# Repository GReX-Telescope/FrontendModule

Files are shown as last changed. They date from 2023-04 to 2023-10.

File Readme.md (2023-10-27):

# GReX Frontend Module

You'll need:
- [Rust](https://rustup.rs/)
- ARM Rust toolchain
    - `rustup target add thumbv7em-none-eabihf`
- [just](https://github.com/casey/just)
    - `cargo install just`
- [cross](https://github.com/cross-rs/cross) (which requires either Docker or Podman)
    - `cargo install cross --git https://github.com/cross-rs/cross`
- [probe-rs](https://probe.rs/)
    - `cargo install probe-rs --features cli,ftdi`

## Hardware

For assembly, access the interactive BOM [here](https://grex-telescope.github.io/FrontendModule/hardware/bom/ibom.html)

## Software

### Building

Build for the current architecture

`just build-cli`

### For the RPi in the box

`just build-cli-pi`

The resulting binary is in `target/armv7-unknown-linux-musleabihf/release/cli` which you can copy to the Pi, `chmod +x` if you need, and run.

## Firmware

### Building

`just build-firmware`

The resulting binary (elf) is in target/thumbv6m-none-eabi/release/firmware

### Flashing

Using a JLink in CMSIS-DAP mode

`just flash-firmware`

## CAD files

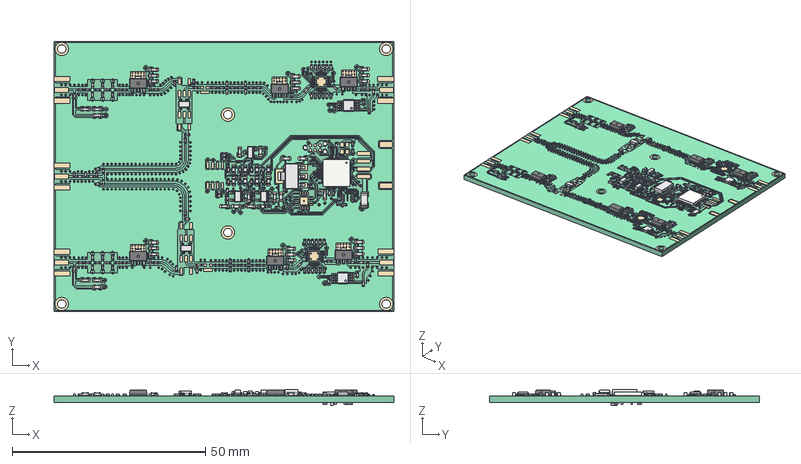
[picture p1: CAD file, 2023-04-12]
hardware/FreeCAD_Render.FCStd
88.0 x 70.0 x 4.27 mm
Pcb_5cf6
topPads_5cf6
topTracks_5cf6
topZones_5cf6
botPads_5cf6
botTracks_5cf6
botZones_5cf6
R35_R_0402_1005Metric_f5f3ad6d96c7 x 39
U27_MSOP_8_3x3mm_P065mm_f5ce7eb6c5d4 x 2
C12_C_0603_1608Metric_8642f7516920 x 30
C99_C_0402_1005Metric_0b61def5e92b x 70
L20_L_0402_1005Metric_fefcc591d3d4 x 34
D1_LED_0603_1608Metric_cfe29d252c61 x 8
R7_R_0603_1608Metric_f544fe8919fd x 3
adbeea57-9c39-11ed-93f0-dde97e994e83_part x 6
adbeea58-9c39-11ed-93f0-dde97e994e83_part x 6
adbeea59-9c39-11ed-93f0-dde97e994e83_part x 6
L6_L_0603_1608Metric_c72d023e8189 x 4
U4_SOT_223_62a9cd10a710
F1_Fuse_1206_3216Metric_ddd44b4a31ef
U7_SOT_23_5_c46f7dd765f9 x 2
U6_QFN_56_1EP_7x7mm_P04mm_EP32x32mm_00caf949446c
U12_SOT_143_13a6a7517807 x 2
U3_SOT_23_b6f0decfda9a

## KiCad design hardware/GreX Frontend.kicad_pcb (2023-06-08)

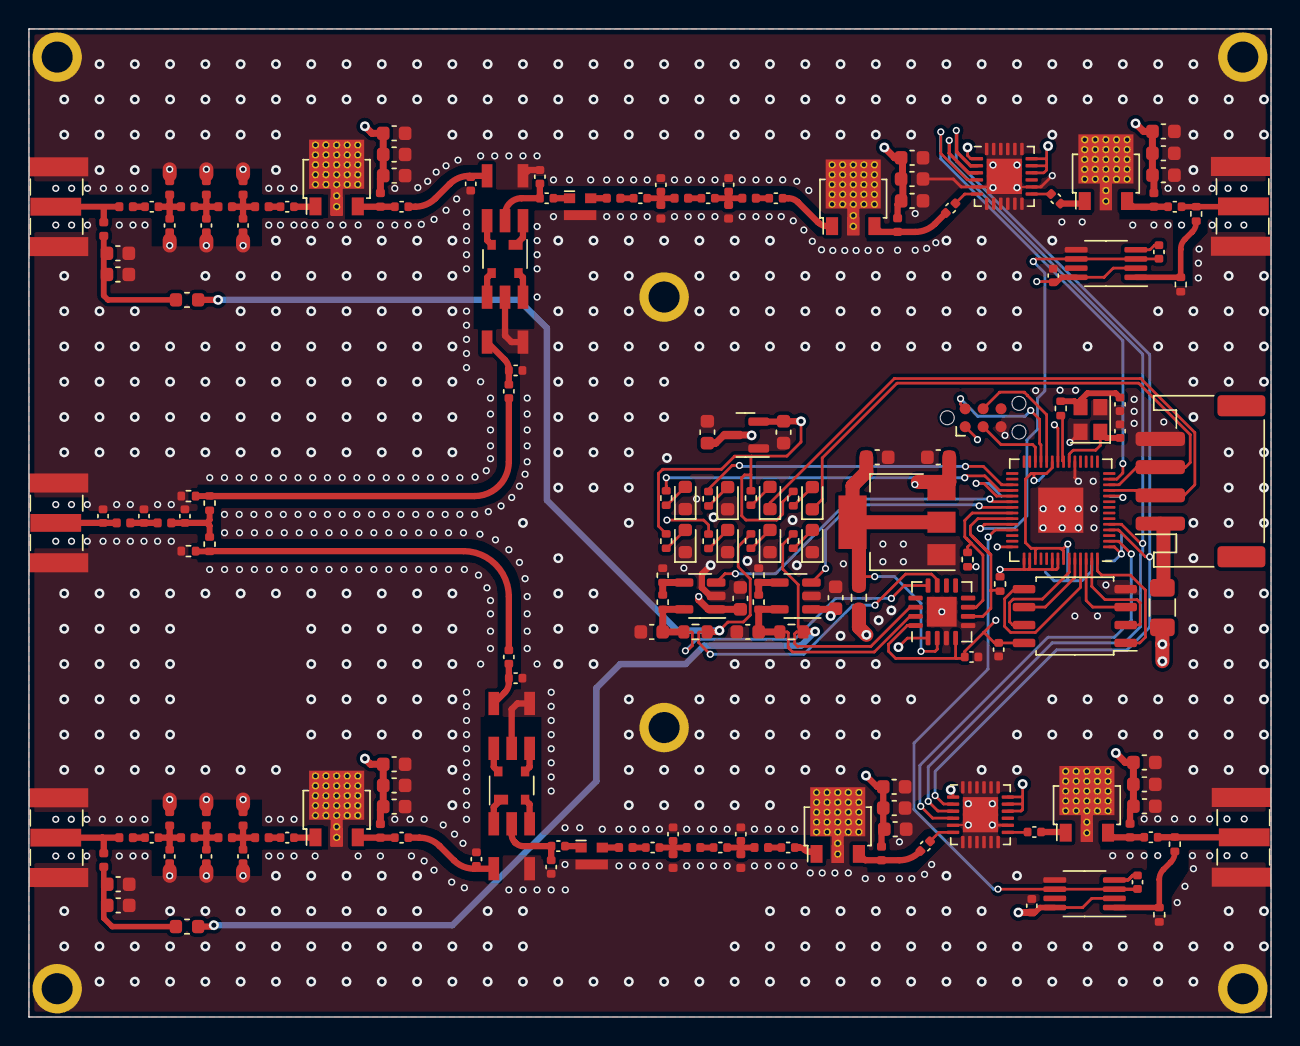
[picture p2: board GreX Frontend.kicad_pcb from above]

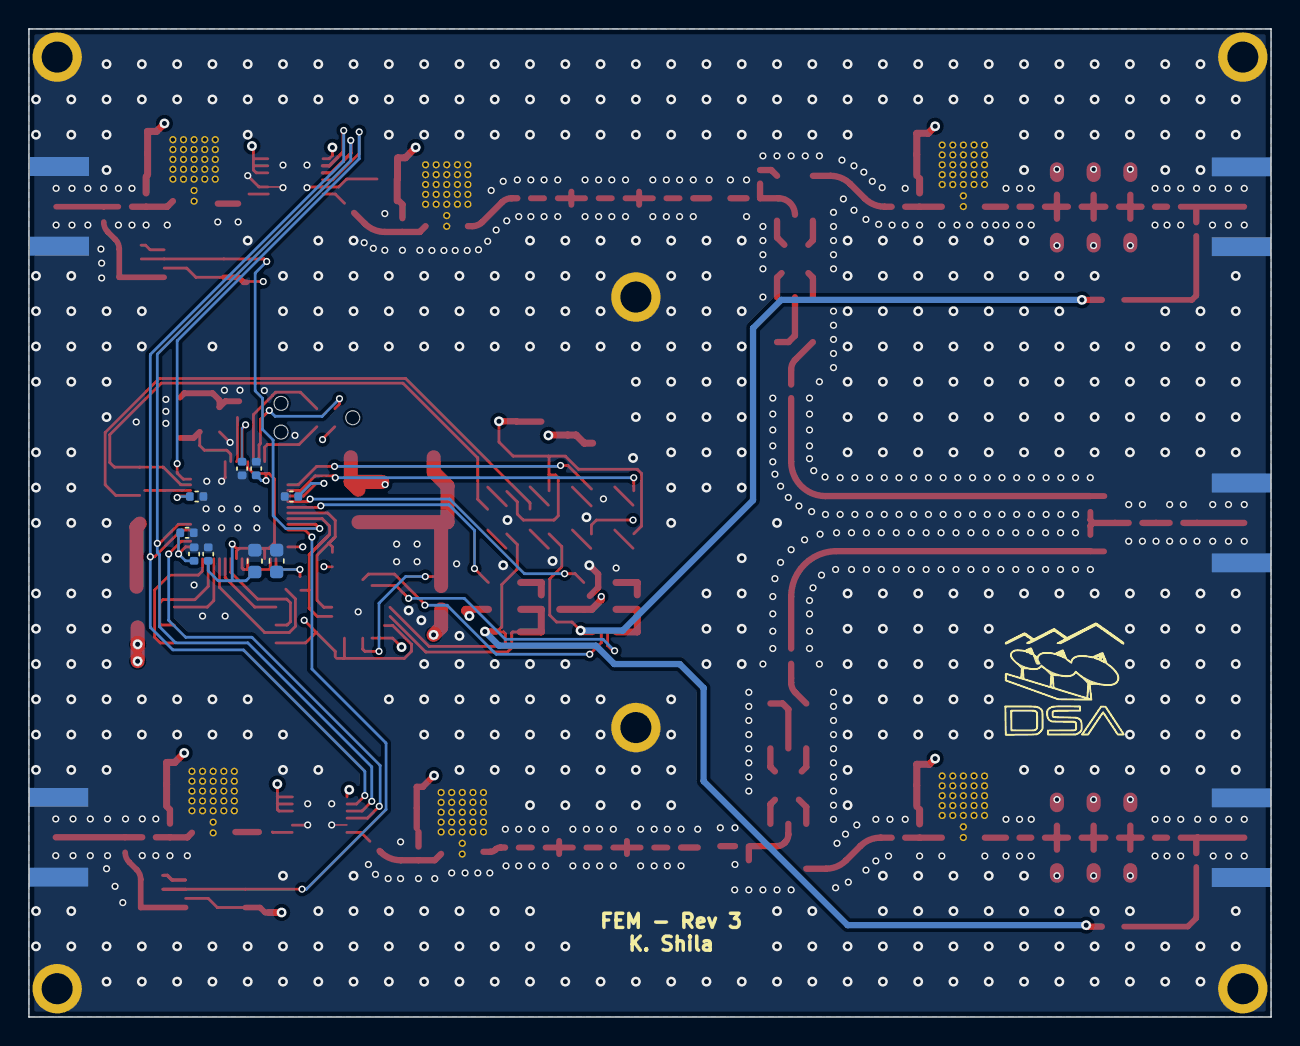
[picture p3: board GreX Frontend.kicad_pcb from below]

Board: 4 copper layers, 88.0 x 70.0 mm, 199 parts (10 on the bottom side), 116 nets.

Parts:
C1, C34, C38, C52, C55, C59, C75, C79: 1.2n; C_0603_1608Metric
C2, C35, C39, C53, C56, C60, C76, C80: 68p; C_0603_1608Metric
C3, C4, C5, C7, C9, C10, C17, C19, C33, C40, C54, C61, C74, C78: 1u; C_0603_1608Metric
C6, C8: 22u; C_0603_1608Metric
C11, C13, C15, C16, C18, C20, C21, C22, C23, C29, C30, C31, C32, C36, C37, C41, C57, C58, C62, C77, C81, C82, C87: 100n; C_0402_1005Metric
C12, C14: 15p; C_0402_1005Metric
C24, C28, C42, C46: 8.2p; C_0402_1005Metric
C25, C27, C43, C45: 16p; C_0402_1005Metric
C26, C44: 3.9p; C_0402_1005Metric
C47, C51, C69, C73: 1.3p; C_0402_1005Metric
C48, C50, C70, C72: 5p; C_0402_1005Metric
C49, C71: 1.6; C_0402_1005Metric
C63, C65: 1.8p; C_0402_1005Metric
C64: 4p; C_0402_1005Metric
C66, C67, C68, C83, C84, C85, C86, C88: DNP; C_0402_1005Metric
D1, D2, D3, D4: RED; LED_0603_1608Metric
D5, D6: GREEN; LED_0603_1608Metric
D7, D8: BLUE; LED_0603_1608Metric
F1: Polyfuse; Fuse_1206_3216Metric
H1, H2, H3, H4, H5, H6: MountingHole_2.2mm_M2_ISO7380_Pad
J1, J4, J5, J6, J7: Conn_Coaxial; SMA_Samtec_SMA-J-P-X-ST-EM1_EdgeMount
J2: Screw_Terminal_01x04; JST_PH_S4B-PH-SM4-TB_1x04-1MP_P2.00mm_Horizontal
J3: PROG; Tag-Connect_TC2030-IDC-NL_2x03_P1.27mm_Vertical
L1, L22: 47u; L_0603_1608Metric
L2, L23, L35, L36: 43n; L_0402_1005Metric
L3, L7, L10, L14: 24n; L_0402_1005Metric
L4, L6, L11, L13: 12n; L_0402_1005Metric
L5, L12: 51n; L_0402_1005Metric
L8, L9, L24, L25: 1000n; L_0402_1005Metric
L15, L21, L28, L34: 8.7n; L_0402_1005Metric
L16, L20, L29, L33: 2.2n; L_0402_1005Metric
L17, L19, L30, L32: 13n; L_0402_1005Metric
L18, L31: 27n; L_0402_1005Metric
L26, L27: 9.1n; L_0402_1005Metric
R1, R3: 82k; R_0402_1005Metric
R2, R4: 24k; R_0402_1005Metric
R5: 0.2; R_0603_1608Metric
R6, R7: 1; R_0603_1608Metric
R8, R9, R10, R11, R12, R13, R14, R15, R16: 1k; R_0402_1005Metric
R17, R18: 4.7k; R_0402_1005Metric
R19, R22: 100; R_0402_1005Metric
R20, R21: 68; R_0402_1005Metric
R23, R25: 226; R_0402_1005Metric
R24, R26: 28; R_0402_1005Metric
U1: DSA_Logo; DSAlogo_letterswhite
U2: XC6206PxxxMR; SOT-23
U3: AMS1117-5.0; SOT-223-3_TabPin2
U4, U5: SPX3819M5-L; SOT-23-5
U6: INA3221; Texas_RGV_S-PVQFN-N16_EP2.1x2.1mm
U7: IS25LP080D-JBLE; SOIC-8_5.275x5.275mm_P1.27mm
U8: RP2040; QFN-56-1EP_7x7mm_P0.4mm_EP3.2x3.2mm
U9, U10: PAT1220-C-3DB; RF_Attenuator_Susumu_PAT1220
U11, U13, U14, U16, U20, U21: ADL5611; SOT89-HighTemp
U12, U15: HMC1122; LFCSP-24-1EP_4x4mm_P0.5mm_EP2.5x2.5mm
U17, U19, U23, U25: TC4-19G2; AT224
U18, U24: BAT-15-099R; SOT-143
U22, U26: AD8314; MSOP-8_3x3mm_P0.65mm
Y1: 2TJ412000NYGBC; Crystal_SMD_2520-4Pin_2.5x2.0mm

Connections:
+1V1: C15.1, C16.1, C17.2, U8.23 (DVDD), U8.45 (VREG_VOUT), U8.50 (DVDD)
+3V3: C7.2, C11.1, C13.1, C18.1, C19.2, C20.1, C21.1, C22.1, C23.1, J3.1, R8.1, R14.1, R15.1, R17.1, R18.1, U2.2 (VO), U6.4 (VS), U6.16 (VPU), U7.8 (VCC), U8.1 (IOVDD), U8.10 (IOVDD), U8.22 (IOVDD), U8.33 (IOVDD), U8.42 (IOVDD), U8.43 (ADC_AVDD), U8.44 (VREG_IN), U8.48 (USB_VDD), U8.49 (IOVDD)
+5VA: C33.2, C34.2, C35.2, C38.2, C39.2, C40.2, C54.2, C55.2, C56.2, C59.2, C60.2, C61.2, C74.2, C75.2, C76.2, C78.2, C79.2, C80.2, C82.2, C87.2, L8.1, L9.1, L24.1, L25.1, L35.1, L36.1, R5.2, R9.1, U6.1 (IN-3), U12.1 (P/S), U12.16 (PUP2), U12.17 (PUP1), U12.18 (VDD), U15.1 (P/S), U15.16 (PUP2), U15.17 (PUP1), U15.18 (VDD), U22.2 (ENBL), U22.8 (VPOS), U26.2 (ENBL), U26.8 (VPOS)
/RF/IF Filter 1 /In: L3.1, U9.2
/RF/IF Filter 1 /Out: C28.2, U11.1
/RF/IF Filter 2/In: L10.1, U10.2
/RF/IF Filter 2/Out: C46.2, U14.1
/RF/Input Stage 1/ADL5611/In: C51.1, U20.1
/RF/Input Stage 1/Input Filter/In: J1.1 (In), L2.2, L15.1
/RF/Input Stage 1/OUT: C77.1, C84.1, U23.4
/RF/Input Stage 2/ADL5611/In: C73.1, U21.1
/RF/Input Stage 2/Input Filter/In: J6.1 (In), L23.2, L28.1
/RF/Input Stage 2/OUT: C66.1, C81.1, U17.6 (PD)
/RF/LO Filter/In: C63.1, J4.1 (In), L26.1
/RF/LO Filter/Out: C65.1, L27.2, R20.1, R21.2
/RF/Mixer/IF: C32.1, C67.1, U17.2 (SCT)
/RF/Mixer/LO: C29.2, C68.1, U19.4
/RF/Mixer_1/IF: C31.1, C85.1, U23.2 (SCT)
/RF/Mixer_1/LO: C30.2, C86.1, U25.6 (PD)
/RF/Output Stage 1/Power Sensor/RF_In: C41.2, J5.1 (In), R23.1
/RF/Output Stage 2/Power Sensor/RF_In: C62.2, J7.1 (In), R25.1
ATTEN_LE_1: U8.13 (GPIO10), U12.4 (LE)
ATTEN_LE_2: U8.2 (GPIO0), U15.4 (LE)
CLK: U8.4 (GPIO2), U12.2 (CLK), U15.2 (CLK)
GND: C1.1, C2.1, C3.1, C4.1, C5.1, C6.1, C7.1, C8.1, C9.1, C10.1, C11.2, C12.2, C13.2, C14.2, C15.2, C16.2, C17.1, C18.2, C19.1, C20.2, C21.2, C22.2, C23.2, C25.2, C27.2, C33.1, C34.1, C35.1, C38.1, C39.1, C40.1, C43.2, C45.2, C48.1, C49.1, C50.1, C52.1, C53.1, C54.1, C55.1, C56.1, C59.1, C60.1, C61.1, C63.2, C64.2, C65.2, C66.2, C67.2, C68.2, C70.1, C71.1, C72.1, C74.1, C75.1, C76.1, C78.1, C79.1, C80.1, C82.1, C84.2, C85.2, C86.2, C87.1, D1.1 (K), D2.1 (K), D3.1 (K), D4.1 (K), D5.1 (K), D6.1 (K), H1.1, H2.1, H3.1, H4.1, H5.1, H6.1, J1.2 (Ext), J2.4, J3.5, J4.2 (Ext), J5.2 (Ext), J6.2 (Ext), J7.2 (Ext), L4.1, L6.1, L11.1, L13.1, L16.2, L18.2, L20.2, L29.2, L31.2, L33.2, R2.2, R4.2, R19.2, R22.1, R24.1, R26.1, U2.1 (GND), U3.1 (GND), U4.2 (GND), U5.2 (GND), U6.3 (GND), U6.5 (A0), U6.17 (EP), U7.4 (GND), U8.19 (TESTEN), U8.57 (GND), U9.3, U10.3, U11.2 (GND), U12.5 (GND), U12.7 (GND), U12.8 (GND), U12.9 (GND), U12.10 (GND), U12.11 (GND), U12.12 (GND), U12.14 (GND), U12.19 (D5), U12.20 (D4), U12.21 (D3), U12.22 (D2), U12.23 (D1), U12.24 (D0), U12.25 (GND), U13.2 (GND), U14.2 (GND), U15.5 (GND), U15.7 (GND), U15.8 (GND), U15.9 (GND), U15.10 (GND), U15.11 (GND), U15.12 (GND), U15.14 (GND), U15.19 (D5), U15.20 (D4), U15.21 (D3), U15.22 (D2), U15.23 (D1), U15.24 (D0), U15.25 (GND), U16.2 (GND), U17.4, U19.2 (SCT), U19.6 (PD), U20.2 (GND), U21.2 (GND), U22.5 (GND), U23.6 (PD), U25.2 (SCT), U25.4, U26.5 (GND), Y1.2, Y1.4
MOSI: U8.5 (GPIO3), U12.3 (SERIN), U15.3 (SERIN)
unnamed: C1.2, C2.2, L1.2, L2.1
unnamed: C14.1, R16.1, Y1.3
unnamed: C24.1, L3.2
unnamed: C24.2, C25.1, L4.2, L5.1
unnamed: C26.1, L5.2
unnamed: C26.2, C27.1, L6.2, L7.1
unnamed: C28.1, L7.2
unnamed: C29.1, R21.1, R22.2
unnamed: C30.1, R19.1, R20.2
unnamed: C31.2, U9.1
unnamed: C32.2, U10.1
unnamed: C36.1, L8.2, U11.3
unnamed: C37.2, U13.1
unnamed: C41.1, L9.2, U13.3
unnamed: C42.1, L10.2
unnamed: C42.2, C43.1, L11.2, L12.1
unnamed: C44.1, L12.2
unnamed: C44.2, C45.1, L13.2, L14.1
unnamed: C46.1, L14.2
unnamed: C47.1, C48.2, L16.1, L17.1
unnamed: C47.2, L15.2
unnamed: C49.2, L17.2, L18.1, L19.1
unnamed: C50.2, L19.2, L20.1, L21.1
unnamed: C51.2, L21.2
unnamed: C52.2, C53.2, L22.2, L23.1
unnamed: C57.1, L24.2, U14.3
unnamed: C58.2, U16.1
unnamed: C62.1, L25.2, U16.3
unnamed: C64.1, L26.2, L27.1
unnamed: C69.1, C70.2, L29.1, L30.1
unnamed: C69.2, L28.2
unnamed: C71.2, L30.2, L31.1, L32.1
unnamed: C72.2, L32.2, L33.1, L34.1
unnamed: C73.2, L34.2
unnamed: C77.2, L35.2, U20.3
unnamed: C81.2, L36.2, U21.3
unnamed: D1.2 (A), R8.2
unnamed: D2.2 (A), R9.2
unnamed: D3.2 (A), R10.2
unnamed: D4.2 (A), R11.2
unnamed: D5.2 (A), R12.2
unnamed: D6.2 (A), R13.2
unnamed: D7.2 (A), R14.2
unnamed: D8.2 (A), R15.2
unnamed: F1.1, J2.1
unnamed: C3.2, C4.2, C5.2, C6.2, F1.2, U2.3 (VI), U3.3 (VI), U4.1 (IN), U5.1 (IN)
unnamed: R1.2, R2.1, U4.4 (ADJ)
unnamed: R3.2, R4.1, U5.4 (ADJ)
unnamed: U7.1 (CE#), U8.56 (QSPI_SS)
unnamed: U7.6 (SCK), U8.52 (QSPI_SCLK)
unnamed: U7.5 (SI_(IO0)), U8.53 (QSPI_SD0)
unnamed: U7.2 (SO_(IO1)), U8.55 (QSPI_SD1)
unnamed: U7.7 (nHOLD_(IO3)), U8.51 (QSPI_SD3)
unnamed: U7.3 (nWP_(IO2)), U8.54 (QSPI_SD2)
unnamed: C12.1, U8.20 (XIN), Y1.1
unnamed: R16.2, U8.21 (XOUT)
unnamed: C37.1, U12.13 (RF_A)
unnamed: C36.2, U12.6 (RF_B)
unnamed: C58.1, U15.13 (RF_A)
unnamed: C57.2, U15.6 (RF_B)
unnamed: U17.1 (S), U18.1
unnamed: U17.3 (SD), U18.2
unnamed: U18.3, U19.1 (S)
unnamed: U18.4, U19.3 (SD)
unnamed: C83.1, U22.4 (FLTR)
unnamed: R23.2, R24.2, U22.1 (RFIN)
unnamed: U23.1 (S), U24.1
unnamed: U23.3 (SD), U24.2
unnamed: U24.3, U25.1 (S)
unnamed: U24.4, U25.3 (SD)
unnamed: C88.1, U26.4 (FLTR)
unnamed: R25.2, R26.2, U26.1 (RFIN)
RF1_IF_POW: C83.2, U8.38 (GPIO26_ADC0), U22.3 (VSSET), U22.6 (V_UP)
RF1_LNA_EN: U4.3 (EN), U8.34 (GPIO22)
RF1_STATUS_LED: R12.1, U8.32 (GPIO21)
RF2_IF_POW: C88.2, U8.39 (GPIO27_ADC1), U26.3 (VSSET), U26.6 (V_UP)
RF2_LNA_EN: U5.3 (EN), U8.35 (GPIO23)
RF2_STATUS_LED: R13.1, U8.31 (GPIO20)
RXD: D8.1 (K), J2.3, U8.12 (GPIO9)
SCL: R18.2, U6.6 (SCL), U8.37 (GPIO25)
SDA: R17.2, U6.7 (SDA), U8.36 (GPIO24)
SWCLK: J3.4, U8.24 (SWCLK)
SWDIO: J3.2, U8.25 (SWD)
TXD: D7.1 (K), J2.2, U8.11 (GPIO8)
VA_+: C8.2, R5.1, U3.2 (VO), U6.2 (IN+3)
VLNA1_+: C9.2, R1.1, R6.1, U4.5 (OUT), U6.12 (IN+1)
VLNA1_-: L1.1, R6.2, R10.1, U6.11 (IN-1)
VLNA2_+: C10.2, R3.1, R7.1, U5.5 (OUT), U6.15 (IN+2)
VLNA2_-: L22.1, R7.2, R11.1, U6.14 (IN-2)
nRESET: J3.3, U8.26 (RUN)

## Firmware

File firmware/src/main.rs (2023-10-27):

#![no_std]
#![no_main]

mod atten;
mod bsp;
mod log_det;
mod mnc;

use bsp::*;
use defmt::*;
use defmt_rtt as _;
use fugit::RateExtU32;
use panic_probe as _;
use postcard::{
    accumulator::{CobsAccumulator, FeedResult},
    to_slice_cobs,
};

// Embedded Hal traits
use embedded_hal::digital::v2::OutputPin;

use hal::{
    adc::{Adc, AdcPin},
    clocks::{init_clocks_and_plls, Clock},
    entry, pac,
    sio::Sio,
    uart::{DataBits, StopBits, UartConfig, UartPeripheral},
    watchdog::Watchdog,
    I2C,
};
use rp2040_hal as hal;

#[entry]
fn main() -> ! {
    info!("FEM Booting!");
    // Setup peripherals, core clocks, etc.
    let mut pac = pac::Peripherals::take().unwrap();
    let _core = pac::CorePeripherals::take().unwrap();
    let mut watchdog = Watchdog::new(pac.WATCHDOG);
    let sio = Sio::new(pac.SIO);

    let clocks = init_clocks_and_plls(
        bsp::XOSC_CRYSTAL_FREQ,
        pac.XOSC,
        pac.CLOCKS,
        pac.PLL_SYS,
        pac.PLL_USB,
        &mut pac.RESETS,
        &mut watchdog,
    )
    .ok()
    .unwrap();

    // Setup the pins
    let pins = bsp::Pins::new(
        pac.IO_BANK0,
        pac.PADS_BANK0,
        sio.gpio_bank0,
        &mut pac.RESETS,
    );

    info!("Setting up ADC");
    // Enable the ADC peripheral and internal temperature sensor
    let mut adc = Adc::new(pac.ADC, &mut pac.RESETS);
    let mut temp_sense = adc.take_temp_sensor().unwrap();

    // Setup RF power monitor chip
    let mut rf1_if_pow = AdcPin::new(pins.rf1_if_pow.into_floating_input());
    let mut rf2_if_pow = AdcPin::new(pins.rf2_if_pow.into_floating_input());

    // Grab the UART pins and setup the peripheral (115200 baud)
    info!("Setting up UART");
    let uart_pins: UartPins = (pins.txd.into_function(), pins.rxd.into_function());
    let uart: Uart = UartPeripheral::new(pac.UART1, uart_pins, &mut pac.RESETS)
        .enable(
            UartConfig::new(115200.Hz(), DataBits::Eight, None, StopBits::One),
            clocks.peripheral_clock.freq(),
        )
        .unwrap();
    info!("Setting up GPIO");
    // Set the LNA outputs to ON by default
    let mut lna_1 = pins.rf1_lna_en.into_push_pull_output();
    let mut lna_2 = pins.rf2_lna_en.into_push_pull_output();
    lna_1.set_high().unwrap();
    lna_2.set_high().unwrap();

    // Set the RF status LEDs to off
    let mut rf1_status_led = pins.rf1_stat_led.into_push_pull_output();
    let mut rf2_status_led = pins.rf2_stat_led.into_push_pull_output();
    rf1_status_led.set_low().unwrap();
    rf2_status_led.set_low().unwrap();

    // Setup the SPI pins and initial state of the latch enable pins (high)
    // pins are implicitly used by the SPI driver
    info!("Setting up SPI");
    let mut atten1_le = pins.atten1_le.into_push_pull_output();
    atten1_le.set_low().unwrap();
    let mut atten2_le = pins.atten2_le.into_push_pull_output();
    atten2_le.set_low().unwrap();

    let spi = hal::Spi::<_, _, _, 6>::new(
        pac.SPI0,
        (pins.sdo.into_function(), pins.clk.into_function()),
    )
    .init(
        &mut pac.RESETS,
        clocks.peripheral_clock.freq(),
        1.MHz(),
        embedded_hal::spi::MODE_0,
    );

    // And setup the two attenuators
    let mut atten = atten::DualHMC624A::new(spi, atten1_le, atten2_le);
    // and set the initial state to 0
    atten.set_attenuation(0.0).unwrap();

    info!("Setting up I2C");
    // Setup I2C for the TMP100 and INA3221
    let i2c = I2C::i2c0(
        pac.I2C0,
        pins.sda.into_function(),
        pins.scl.into_function(),
        400.kHz(),
        &mut pac.RESETS,
        &clocks.system_clock,
    );

    // Setup the INA3221
    let mut ina3221 = ina3221::INA3221::new(i2c, ina3221::AddressPin::Gnd);
    match ina3221.reset() {
        Ok(_) => (),
        Err(_) => error!("INA3221 failed to reset"),
    };
    match ina3221.set_averaging(ina3221::registers::Averages::_256) {
        Ok(_) => (),
        Err(_) => error!("INA3221 failed to set averages"),
    };

    // Setup state for if good and monitor
    let mut state = mnc::State::default();

    // Setup the state for the COBS input message accumulator
    let mut in_buf = [0u8; 256];
    let mut out_buf = [0u8; 256];
    let mut cobs_buf: CobsAccumulator<256> = CobsAccumulator::new();

    info!("FEM Booted, starting main thread!");

    loop {
        // Update monitor payload in state
        mnc::update_monitor_payload(
            &mut state.last_monitor,
            &mut adc,
            &mut rf1_if_pow,
            &mut rf2_if_pow,
            &mut temp_sense,
            &mut ina3221,
        );
        // If there are bytes for us, push them to the accumulator
        if uart.uart_is_readable() {
            while let Ok(n) = uart.read_raw(&mut in_buf) {
                let buf = &in_buf[..n];
                let mut window = buf;
                'cobs: while !window.is_empty() {
                    window = match cobs_buf.feed::<transport::Command>(window) {
                        FeedResult::Consumed => break 'cobs,
                        FeedResult::OverFull(new_wind) => new_wind,
                        FeedResult::DeserError(new_wind) => new_wind,
                        FeedResult::Success {
                            data: cmd,
                            remaining,
                        } => {
                            // Handle command
                            info!("New incoming payload - {}", cmd);

                            match cmd {
                                transport::Command::Monitor => {
                                    // Serialize the last monitor payload
                                    let resp =
                                        transport::Response::Monitor(state.last_monitor.clone());
                                    info!("Sending monitor data - {}", resp);
                                    let s = to_slice_cobs(&resp, &mut out_buf).unwrap();
                                    uart.write_full_blocking(s);
                                }
                                transport::Command::Control(action) => {
                                    // Do the control thing
                                    match action {
                                        transport::Action::SetIfLevel(level) => {
                                            state.if_good_threshold = level
                                        }
                                        transport::Action::Lna1Power(en) => {
                                            if en {
                                                lna_1.set_high().unwrap();
                                            } else {
                                                lna_1.set_low().unwrap();
                                            }
                                        }
                                        transport::Action::Lna2Power(en) => {
                                            if en {
                                                lna_2.set_high().unwrap();
                                            } else {
                                                lna_2.set_low().unwrap();
                                            }
                                        }
                                        transport::Action::SetAtten(a) => {
                                            match atten.set_attenuation(a) {
                                                Ok(_) => (),
                                                Err(_) => error!("Failed to set attenuation"),
                                            }
                                        }
                                    }
                                    // Then send an ack
                                    let resp = transport::Response::Ack;
                                    let s = to_slice_cobs(&resp, &mut out_buf).unwrap();
                                    uart.write_full_blocking(s);
                                }
                            }
                            remaining
                        }
                    };
                }
            }
        }
        // Set the RF Good LEDs
        if state.last_monitor.if1_power >= state.if_good_threshold {
            rf1_status_led.set_high().unwrap();
        } else {
            rf1_status_led.set_low().unwrap();
        }
        if state.last_monitor.if2_power >= state.if_good_threshold {
            rf2_status_led.set_high().unwrap();
        } else {
            rf2_status_led.set_low().unwrap();
        }
    }
}

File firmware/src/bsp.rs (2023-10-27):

use embedded_hal::adc::{Channel, OneShot};
use hal::{pac::UART1, Adc};
use rp2040_hal as hal;

// Crystal freq
pub const XOSC_CRYSTAL_FREQ: u32 = 12_000_000;

/// Reference voltage for ADC conversions
pub const ADC_REF_VOLT: f32 = 3.3;

// Don't forget the second stage bootloader
#[link_section = ".boot2"]
#[no_mangle]
#[used]
pub static BOOT2_FIRMWARE: [u8; 256] = rp2040_boot2::BOOT_LOADER_IS25LP080;

// And add all of our pins!
hal::bsp_pins!(
    Gpio20 { name: rf1_stat_led },
    Gpio21 { name: rf2_stat_led },
    Gpio22 { name: rf1_lna_en },
    Gpio23 { name: rf2_lna_en },
    Gpio26 { name: rf1_if_pow },
    Gpio27 { name: rf2_if_pow },
    Gpio8 {
        name: txd,
        aliases: { FunctionUart, PullDown: Txd }
    },
    Gpio9 {
        name: rxd,
        aliases: { FunctionUart, PullDown: Rxd }
    },
    Gpio24 {
        name: sda,
        aliases: { FunctionI2C, PullUp: Sda}
    },
    Gpio25 {
        name: scl,
        aliases: { FunctionI2C, PullUp: Scl}
    },
    Gpio2 {
        name: clk,
        aliases: { FunctionSpi, PullNone: Clk}
    },
    Gpio3 {
        name: sdo,
        aliases: { FunctionSpi, PullNone: Sdo}
    },
    Gpio0 { name: atten2_le },
    Gpio10 { name: atten1_le },
);

// Some type aliases
pub type UartPins = (Txd, Rxd);
pub type Uart = hal::uart::UartPeripheral<hal::uart::Enabled, UART1, UartPins>;

/// Get the 0..1 scaled floating point number representing the 12 bit ADC value
pub fn read_adc<PIN>(adc: &mut Adc, pin: &mut PIN) -> Result<f32, ()>
where
    PIN: Channel<Adc, ID = u8>,
{
    // Read the counts
    let counts: u16 = adc.read(pin).map_err(|_| ())?;
    // Scale raw 12-bit format to 0 .. 1
    let scaled = f32::from(counts) / f32::from(1u16 << 12);
    Ok(scaled.clamp(0.0, 1.0))
}

/// Read the internal temperature sensor in degrees C
pub fn read_temp<PIN>(adc: &mut Adc, pin: &mut PIN) -> Result<f32, ()>
where
    PIN: Channel<Adc, ID = u8>,
{
    // Get the raw voltage
    let v = read_adc(adc, pin)? * ADC_REF_VOLT;
    // RP2040 Datasheet 4.9.5
    Ok(27.0 - (v - 0.706) / 0.001721)
}

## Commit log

2023-01-13 voltage monitoring works
2023-01-14 calibration control
2023-03-30 Add PCB design
    [GreX Frontend-F_Cu.gtl, GreX Frontend-NPTH.drl, GreX Frontend-PTH.drl, GreX Frontend-job.gbrjob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]
2023-04-12 FEM v3 Updates
    [FreeCAD_Render.FCStd, GreX Frontend-F_Cu.gtl, GreX Frontend-NPTH.drl, GreX Frontend-PTH.drl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]
2023-05-10 Remove cal circuit, swap attens, swap norflash
    [GreX Frontend.kicad_pcb, input.kicad_sch, mcu.kicad_sch, output.kicad_sch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]
2023-05-26 Fix BOM errors
    [mcu.kicad_sch, power.kicad_sch]
2023-06-08 Update FEM hardware design for production version
    [GreX Frontend.kicad_pcb, GreX Frontend.kicad_sch, IF Filter.kicad_sch, adl5611.kicad_sch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]
